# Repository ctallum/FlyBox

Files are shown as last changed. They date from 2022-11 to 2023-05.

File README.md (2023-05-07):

# FlyBox - Olin Brandeis Rosbash Lab HMMI FlyBox Redesign SCOPE Project

# About the Firmware
All the source code and documentation for the FlyBox firmware can be found [here](https://github.com/ctallum/FlyBox-firmware)

# About the Web UI
All the source code and documentation for the webside can be found [here](https://github.com/ctallum/FlyBox/tree/main/programming-gui)

## Test Creator Website
To access the website, visit:
https://rosbash-lab-flybox.github.io/FlyBox/

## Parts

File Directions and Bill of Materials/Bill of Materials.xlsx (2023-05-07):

 |  | FlyBox Bill of Materials |  | Total Items | Total Cost | Chris Allum, Olivia Jo Bradley, S. C. "Mack" McAneney, Zachary Sherman, Florian Schwarzinger
 |  |  |  | 207 | $735.16
Subsystem | Custom | Item | Cost Per Unit | Quantity | Total Cost | Source | Notes
PCB | TRUE | Main PCB | $80.00 | 1 | $61.41 | PCBWay (https://www.pcbway.com/project/shareproject/W547848AS1D13_MainBoardGerber3_5fe985dc.html) | Price with assembly and an order size of 5, may change slightly
PCB | TRUE | IR and fans PCB | $50.00 | 1 | $43.14 | PCBWay (https://www.pcbway.com/project/shareproject/FlyBox_IR_Board_50aa739c.html) | Price with assembly and an order size of 5, may change slightly
PCB | TRUE | RGW LED PCB | $50.00 | 1 | $51.54 | PCBWay (https://www.pcbway.com/project/shareproject/FlyBox_RGW_Board_fc0900b7.html) | Price with assembly and an order size of 5, may change slightly
Miscellaneous | FALSE | Zipties | $6.99 | 1 | $6.99 | Amazon (http://www.amzn.com/B08TVLYB3Q)
Miscellaneous | FALSE | IR filter for camera | $0.05 | 1 | $0.05 | ePlastics (https://www.eplastics.com/plexiglass/acrylic-sheets/ACRY31430-125PM11-555X11-850) | We believe this product will work, but we have been using filters provided by Brandeis
Miscellaneous | FALSE | Electric screwdriver | $25.99 | 1 | $25.99 | Amazon (https://www.amazon.com/Electric-Screwdriver-Cordless-Precision-Rechargeable/dp/B08X9V5K2V)
Miscellaneous | FALSE | Cyanoacrylate glue | $13.99 | 1 | $13.99 | Amazon (https://www.amazon.com/dp/B01MDNS8QB?tag=architecture_lab-20&linkCode=ogi&th=1)
Frame Raw Materials | FALSE | 12"x24"x1/4" black acrylic sheet | $21.13 | 6 | $126.78 | McMaster (https://www.mcmaster.com/8505K755-8505K923/)
Frame Raw Materials | FALSE | 1/8" translucent white acrylic (12"x24" sheet) | $15.40 | 1 | $15.40 | McMaster (https://www.mcmaster.com/8505K742/)
Frame Raw Materials | FALSE | Black felt (≥13"x13") | $4.50 | 1 | $4.50 | Amazon (https://www.amzn.com/B07MPQ29TB) | One sheet of felt has enough material for four boxes
Frame Raw Materials | TRUE | 3D print - fan baffle |  | 2 | $0.00 | n/a
Frame Raw Materials | TRUE | 3D print - camera mount |  | 1 | $0.00 | n/a
Frame Raw Materials | TRUE | 3D print - SD card and rotary encoder piece |  | 1 | $0.00 | n/a
Frame Raw Materials | TRUE | 3D print - display and PCB spacer |  | 14 | $0.00 | n/a
Frame Raw Materials | FALSE | J-B Weld 31319 RTV silicone | $7.45 | 1 | $7.45 | Amazon (https://www.amzn.com/B00ID8F8E4)
Frame Hardware | FALSE | Feet (with provided screws) | $1.00 | 4 | $4.00 | Amazon (https://www.amzn.com/B08PCGXKK9) | Come in 12 pack
Frame Hardware | FALSE | Acrylic hinges | $0.42 | 2 | $0.85 | Amazon (https://www.amzn.com/B09B3GNV9T) | Come in 20 pack
Frame Hardware | FALSE | Latch | $2.25 | 1 | $2.25 | Amazon (http://www.amzn.com/B01MR126O6) | Come in 4 pack
Frame Hardware | FALSE | M2x6 cap head screw | $0.10 | 4 | $0.39 | McMaster (https://www.mcmaster.com/91292A831/)
Frame Hardware | FALSE | M3x12 round head screw | $0.07 | 8 | $0.54 | McMaster (https://www.mcmaster.com/92095A183/) | Come in 100 pack
Frame Hardware | FALSE | M3x16 round head screw | $0.09 | 20 | $1.86 | McMaster (https://www.mcmaster.com/92095A184/) | Come in 100 pack
Frame Hardware | FALSE | M3x20 round head screw | $0.11 | 28 | $2.97 | McMaster (https://www.mcmaster.com/92095A185/) | Come in 50 pack
Frame Hardware | FALSE | M3x35 standoff | $2.91 | 4 | $11.64 | McMaster (https://www.mcmaster.com/95947A519/)
Frame Hardware | FALSE | M3 nut | $0.03 | 48 | $1.26 | McMaster (https://www.mcmaster.com/90592A085/) | Come in 100 pack
Frame Hardware | FALSE | M4x12 round head screw | $0.13 | 2 | $0.27 | McMaster (https://www.mcmaster.com/92095A192/) | Come in 100 pack
Frame Hardware | FALSE | M4x20 round head screw | $0.17 | 2 | $0.35 | McMaster (https://www.mcmaster.com/92095A196/) | Come in 50 pack
Frame Hardware | FALSE | M4 nut | $0.03 | 4 | $0.13 | McMaster (https://www.mcmaster.com/90592A090/) | Come in 100 pack
Electronics | FALSE | USB A-male to micro-B-male cable - 6 feet | $7.41 | 1 | $7.41 | Amazon (https://www.amazon.com/AmazonBasics-Male-Micro-Cable-Black/dp/B07232M876?th=1)
Electronics | FALSE | ESP32 microcontroller | $7.00 | 1 | $7.00 | Amazon (https://www.amzn.com/B09GK74F7N)
Electronics | FALSE | SPI SD card reader | $0.89 | 1 | $0.89 | Amazon (https://www.amzn.com/B0B7WZQVHS) | "Welding" should be selected to avoid needing to solder
Electronics | FALSE | RTC DS3231 real time clock | $4.60 | 1 | $4.60 | Amazon (http://www.amzn.com/B09KPC8JZQ)
Electronics | FALSE | Bi-directional logic level converter | $7.95 | 1 | $7.95 | Adafruit (https://www.adafruit.com/product/395)
Electronics | FALSE | 12V DC buck converter | $7.50 | 1 | $7.50 | Amazon (http://www.amzn.com/B07XXWQ49N)
Electronics | FALSE | 20x4 I2C display module | $10.99 | 1 | $10.99 | Amazon (http://www.amzn.com/B07QLRD3TM)
Electronics | FALSE | 3021-D-E-1000 BuckPuck | $10.99 | 4 | $43.96 | LuxeonStar (https://www.luxeonstar.com/1000ma-externally-dimmable-buckpuck-dc-driver)
Electronics | FALSE | 5K audio potentiometer | $2.50 | 1 | $2.50 | Adafruit (https://www.adafruit.com/product/5284)
Electronics | FALSE | Red LED strip | $11.88 | 1 | $11.88 | Waveform (https://store.waveformlighting.com/collections/led-strips/products/simplecolor-red-led-strip-lights) | Only using a fraction of the roll per box
Electronics | FALSE | Green LED strip | $11.88 | 1 | $11.88 | Waveform (https://store.waveformlighting.com/collections/simplecolor/products/simplecolor-green-led-strip-lights) | Only using a fraction of the roll per box
Electronics | FALSE | White LED strip | $6.81 | 1 | $6.81 | Waveform (https://store.waveformlighting.com/collections/led-strips/products/filmgrade-led-strip-lights-for-film-photography?variant=13809653186662) | Only using a fraction of the roll per box
Electronics | FALSE | IR LED strip | $12.64 | 1 | $12.64 | Waveform (https://store.waveformlighting.com/collections/led-strips/products/infrared-850-nm-ir-led-strip-light?variant=13726854578278) | Only using a fraction of the roll per box
Electronics | FALSE | LED strip clasps | $0.96 | 13 | $12.47 | Amazon (https://www.amazon.com/Solderless-Connector-Terminal-Screwdriver-Included/dp/B09Y91QCQR)
Electronics | FALSE | Assorted breadboard jumper wires | $6.99 | 1 | $6.99 | Amazon (http://www.amzn.com/B07GD2BWPY)
Electronics | FALSE | Noctua NF-A4x10 PWM fans | $14.95 | 4 | $59.80 | Amazon (https://www.amzn.com/B07DXRNYNX)
Electronics | FALSE | Power switch | $0.58 | 1 | $0.58 | Amazon (https://www.amzn.com/B08Q3WJW8Q)
Electronics | FALSE | DC power jack | $1.52 | 1 | $1.52 | Amazon (https://www.amazon.com/5-5mm-Supply-Socket-Female-Connection/dp/B082GHXS1Q) | Pack of 5, only using one per box
Electronics | FALSE | Rotary encoder | $2.00 | 1 | $2.00 | Amazon (https://www.amzn.com/B07F26CT6B)
Electronics | FALSE | Adafruit 4121 USB passthrough | $5.95 | 1 | $5.95 | Adafruit (https://www.adafruit.com/product/4212)
Electronics | FALSE | USB A-male to B-male cable - 6 feet | $6.29 | 1 | $6.29 | Amazon (https://www.amzn.com/B00NH11KIK)
Electronics | FALSE | Logitech C920 webcam | $64.90 | 1 | $64.90 | Amazon (http://www.amzn.com/B006JH8T3S)
Electronics | FALSE | 90 degree pin headers | $8.49 | 1 | $8.49 | Amazon (https://www.amazon.com/Generic-Female-Header-Arduino-LilyPad/dp/B00OE8GTQ8)
Electronics | FALSE | Male barrel jack adapter | $5.97 | 1 | $5.97 | Amazon (https://www.amazon.com/Barrel-Connector-Cameras-Single-LED/dp/B01M1YA9ST?s=electronics)
Electronics | FALSE | WAGO solderless inline wire connector | 25.39 | 1 | 25.39 | Amazon (https://www.amazon.com/221-2401-WAGO-Lever-Nuts%C2%AE-2-Conductor-Transparent/dp/B0BKR2SR7H) | Only using a few per box
Electronics | FALSE | RTC battery | $7.59 | 1 | $7.59 | Amazon (https://www.amazon.com/Procter-Gamble-DURDL2032B4PK-Duracell-Lithium/dp/B009108SGS?s=electronics) | Only using one per box
Electronics | FALSE | Ribbon Wire | $1.00 | 1 | $1.00 | Amazon (https://www.amazon.com/AOTOINK-Conductor-Extension-Welding-Tinned/dp/B08JTZCJV1) | Only using a fraction of the roll per box
Electronics | FALSE | Power supply | $6.50 | 1 | $6.50 | Amazon (https://www.amazon.com/100-240V-Transformers-Switching-Applications-Connectors/dp/B077PW5JC3?s=electronics) | Pack of 2, only using 1

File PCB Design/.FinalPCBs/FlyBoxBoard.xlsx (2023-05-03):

 |  |  | T-1D14W547848A BOM
Item # | *Designator | *Qty | Manufacturer | *Mfg Part # | Description / Value | *Package/Footprint | Type | Your Instructions / Notes
1 | 5V in, 12V in, RED, GREEN, INFRARED, WHITE | 6 | Würth Elektronik, from digikey | 691213510002 | 2 Pin 5.08 screw terminal |  | Thru Hole | Arrange the component so the screw terminals face the outer edge of the board
2 | FANS, LCD Screen | 2 | Würth Elektronik, from digikey | 691241510004 | 4 Pin 5.08 screw terminal |  | Thru Hole | Arrange the component so the screw terminals face the outer edge of the board
3 | Hours, Minutes | 2 | TE Connectivity ALCOSWITCH Switches | 1571563-2 | SWITCH TACTILE SPST-NO 0.05A 24V | SW_1571563-2 | SMD
4 | BuckPuck IR, BuckPuck Green, BuckPuck Red, BuckPuck White | 4 | Sullins Connector Solutions | PPPC071LFBN-RC | CONN HDR 7POS FEMALE |  | Thru Hole
5 | Logic Level Right Side HV, Logic Level Left Side HV, | 2 | Würth Elektronik, from digikey | 61301011821 | CONN HDR 10POS FEMALE |  | Thru Hole
5 | 5V, 12V, ESP 32 unused pins, Potentiometer, Potentiometer, GND, ESP 32 unused pins, | 7 | Würth Elektronik, from digikey | 61300511821 (https://www.pcbway.com/components/detail/61300511821/732960/) | CONN HDR 5POS FEMALE |  | Thru Hole
6 | Real Time Controller | 1 | Würth Elektronik, from digikey | 61300611821 (https://www.pcbway.com/components/detail/61300611821/437679/) | CONN HDR 6POS FEMALE |  | Thru Hole
7 | ESP 32 Left Side extra pinouts | 1 | Würth Elektronik, from digikey | 62000211821 (https://www.digikey.com/en/products/detail/w%C3%BCrth-elektronik/62000211821/15672178) | CONN HDR 2POS FEMALE |  | Thru Hole
8 | Logic Level LV pins, Logic Level HV pins | 2 | Würth Elektronik, from digikey | 61300311821 (https://www.pcbway.com/components/detail/61300311821/1044014/) | CONN HDR 3POS FEMALE |  | Thru Hole
9 | ESP 32 Left Side, ESP 32 Right Side | 2 | Sullins Connector Solutions | PPTC151LFBN-RC | CONN HDR 15POS FEMALE |  | Thru Hole
10 | 5KOhms | 8 | Stackpole Electronics Inc (https://www.digikey.com/en/supplier-centers/stackpole-electronics) | RNCP0805FTD4K99 | 5k ohm SMD resistor 0805/2012 metric | 0805 | SMD
 | Rotary Knob | 1 | Phoenix Contact (https://www.digikey.com/en/supplier-centers/phoenix-contact) | 1729157 | 5 Pin 5.08 screw terminal |  | Thru Hole | Arrange the component so the screw terminals face the outer edge of the board
 | SD card reader | 1 | Phoenix Contact (https://www.digikey.com/en/supplier-centers/phoenix-contact) | 1729160 | 6 Pin 5.08 screw terminal |  | Thru Hole | Arrange the component so the screw terminals face the outer edge of the board
 | Transistor, Transistor, Transistor, Transistor | 4 | STMicroelectronics from digikey | 2N3906 (https://www.pcbway.com/components/detail/2N3906/289442/) | 2N3906 Transistor |  | Thru Hole
 | Transistor, Transistor, Transistor, Transistor | 4 | Digikey (Micro Commercial Co) | 2N3906-AP (https://www.pcbway.com/components/detail/2N3906AP/883195/) | 2N3906 Transistor |  | Thru Hole | https://www.pcbway.com/components/detail/2N3906AP/883195/

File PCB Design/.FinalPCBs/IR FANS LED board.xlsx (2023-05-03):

 |  |  | T-1D18W547848A BOM
Item # | *Designator | *Qty | Manufacturer | *Mfg Part # | Description / Value | *Package/Footprint | Type | Your Instructions / Notes
1 | IR, IR, IR, IR from above | 4 | Würth Elektronik, from digikey | 691213510002 | 2 Pin 5.08 screw terminal |  | Thru Hole | Arrange the component so the screw terminals face the outer edge of the board
2 | Fans, Fans, Fans, Fans, | 4 | Würth Elektronik, from digikey | 61300411121 (https://www.digikey.com/en/products/detail/w%C3%BCrth-elektronik/61300411121/4846827) | 4 Pin 2.54 male header pins |  | Thru Hole | Arrange the longer ends of the pins up on the board
2 | Fans from above | 1 | Würth Elektronik, from digikey | 691241510004 | 4 Pin 5.08 screw terminal |  | Thru Hole | Arrange the component so the screw terminals face the outer edge of the board

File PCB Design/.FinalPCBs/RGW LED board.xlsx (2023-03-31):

 |  |  | T-1D16W547848A BOM
Item # | *Designator | *Qty | Manufacturer | *Mfg Part # | Description / Value | *Package/Footprint | Type | Your Instructions / Notes
1 | - R strip +, - G strip +, - R from above +, - W strip +, - G from above +, - W from above +, | 13 | Würth Elektronik, from digikey | 691213510002 | 2 Pin 5.08 screw terminal |  | Thru Hole | Arrange the component so the screw terminals face the outer edge of the board

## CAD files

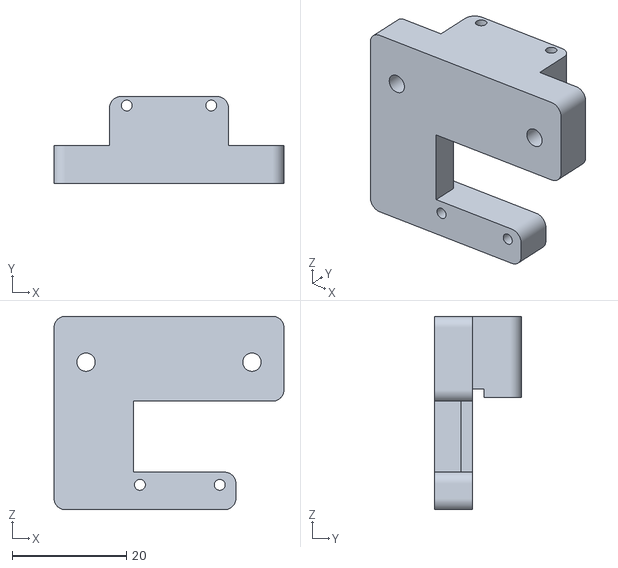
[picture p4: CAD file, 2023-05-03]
fabrication-files/3d-print-files/SD_card_and_rotary_encoder_mount.stl
40.2 x 15.2 x 33.8

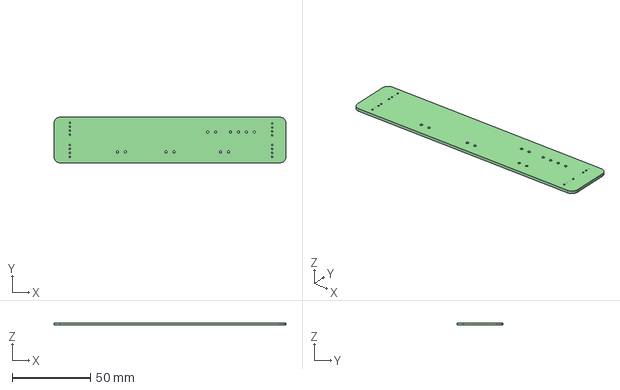
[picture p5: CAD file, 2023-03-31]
PCB Design/IR FANS LED board.step
148.6 x 29.2 x 1.60 mm

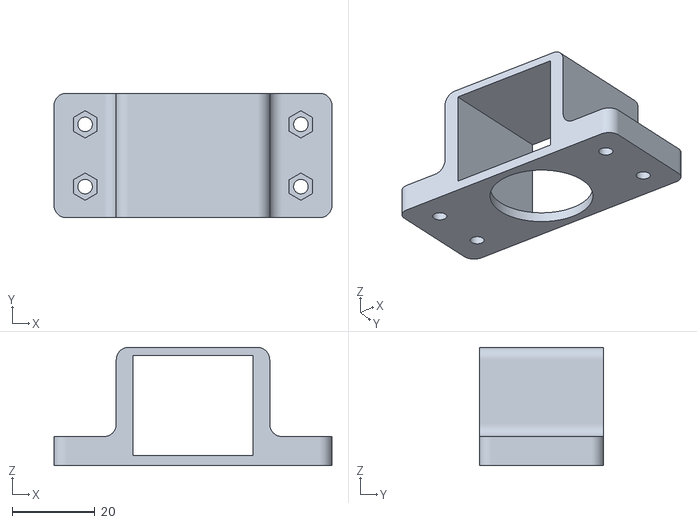
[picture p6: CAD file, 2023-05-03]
fabrication-files/3d-print-files/camera_mount.stl
67.0 x 30.0 x 28.5

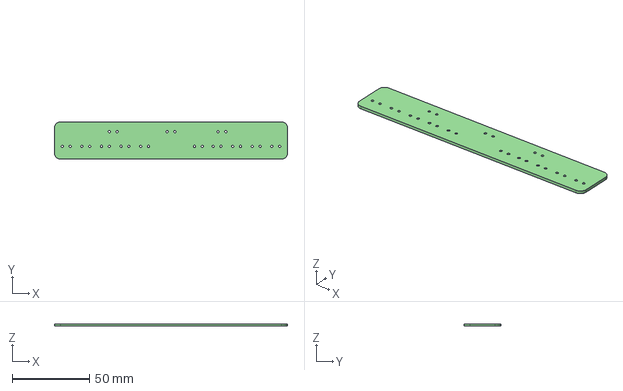
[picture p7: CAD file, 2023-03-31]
PCB Design/RGW LED board.step
151.1 x 24.1 x 1.60 mm

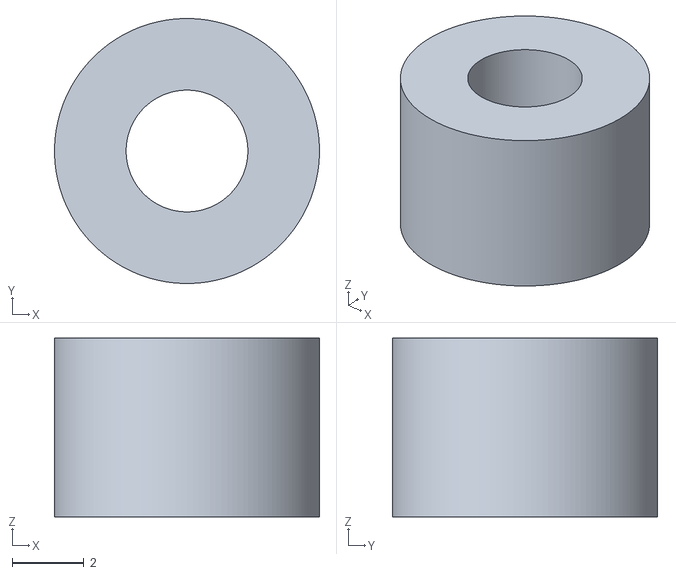
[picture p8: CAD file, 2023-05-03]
fabrication-files/3d-print-files/spacer.stl
7.40 x 7.40 x 4.99

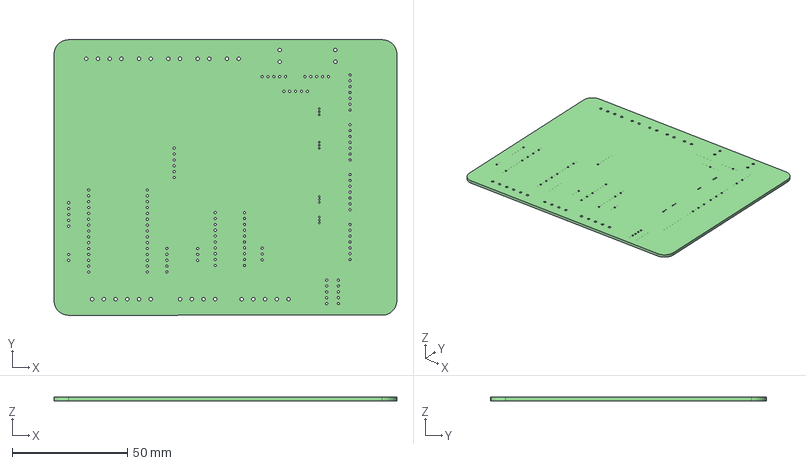
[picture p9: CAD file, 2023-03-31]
PCB Design/FlyBoxBoard.step
148.6 x 119.4 x 1.60 mm

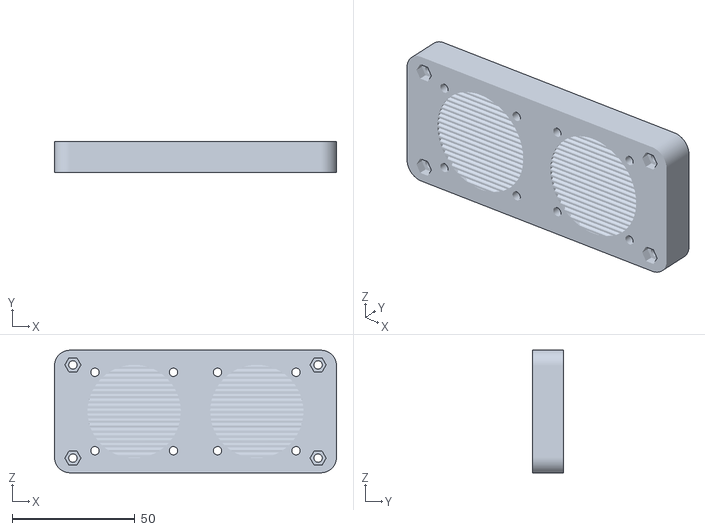
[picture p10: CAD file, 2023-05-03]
fabrication-files/3d-print-files/fan_baffle.stl
115.0 x 12.7 x 50.0

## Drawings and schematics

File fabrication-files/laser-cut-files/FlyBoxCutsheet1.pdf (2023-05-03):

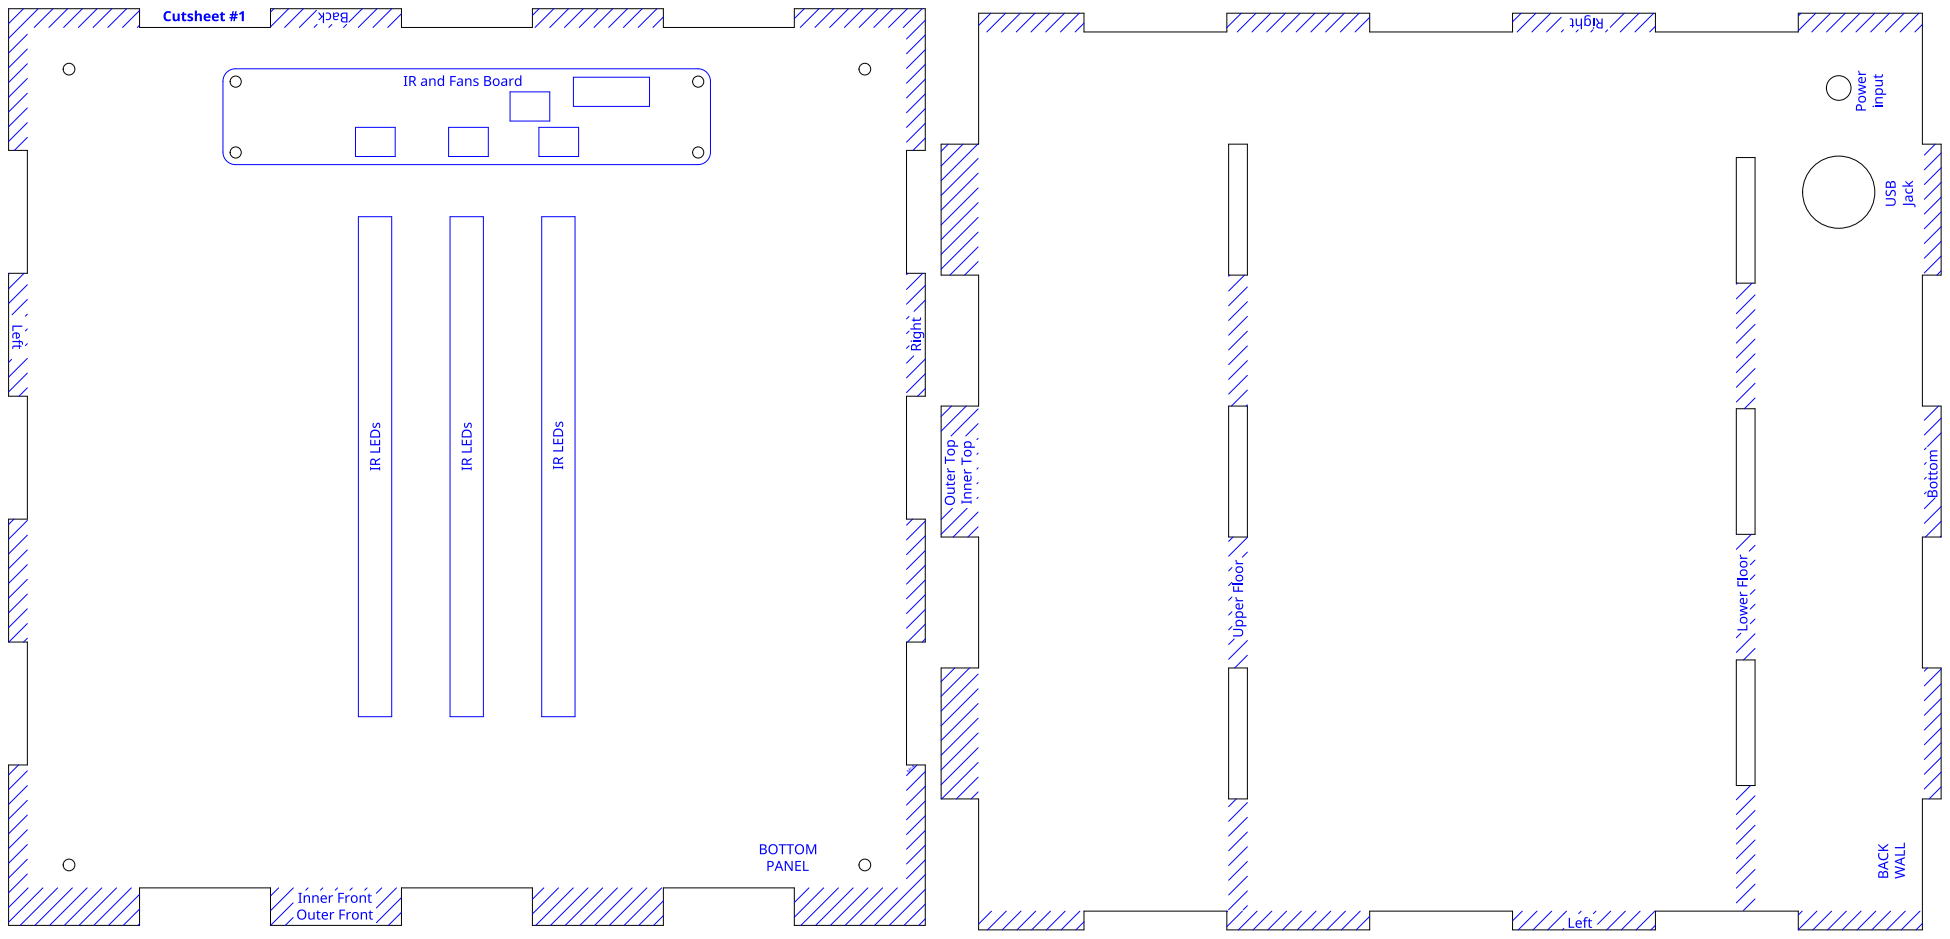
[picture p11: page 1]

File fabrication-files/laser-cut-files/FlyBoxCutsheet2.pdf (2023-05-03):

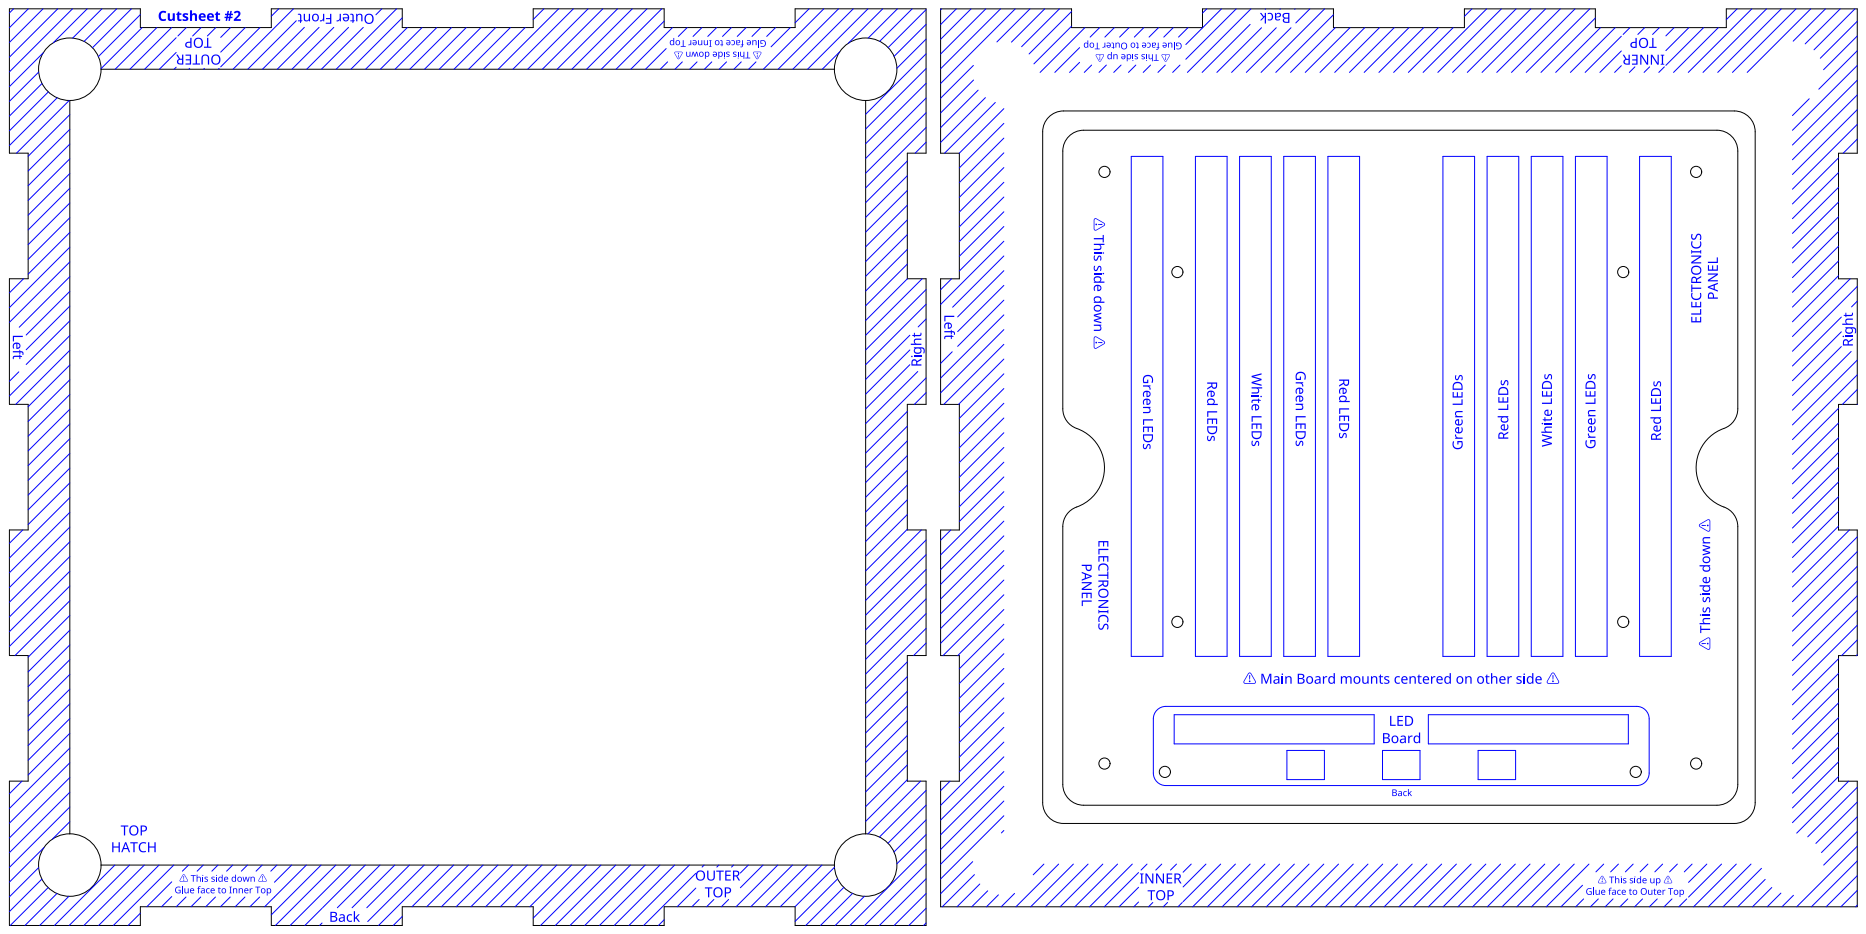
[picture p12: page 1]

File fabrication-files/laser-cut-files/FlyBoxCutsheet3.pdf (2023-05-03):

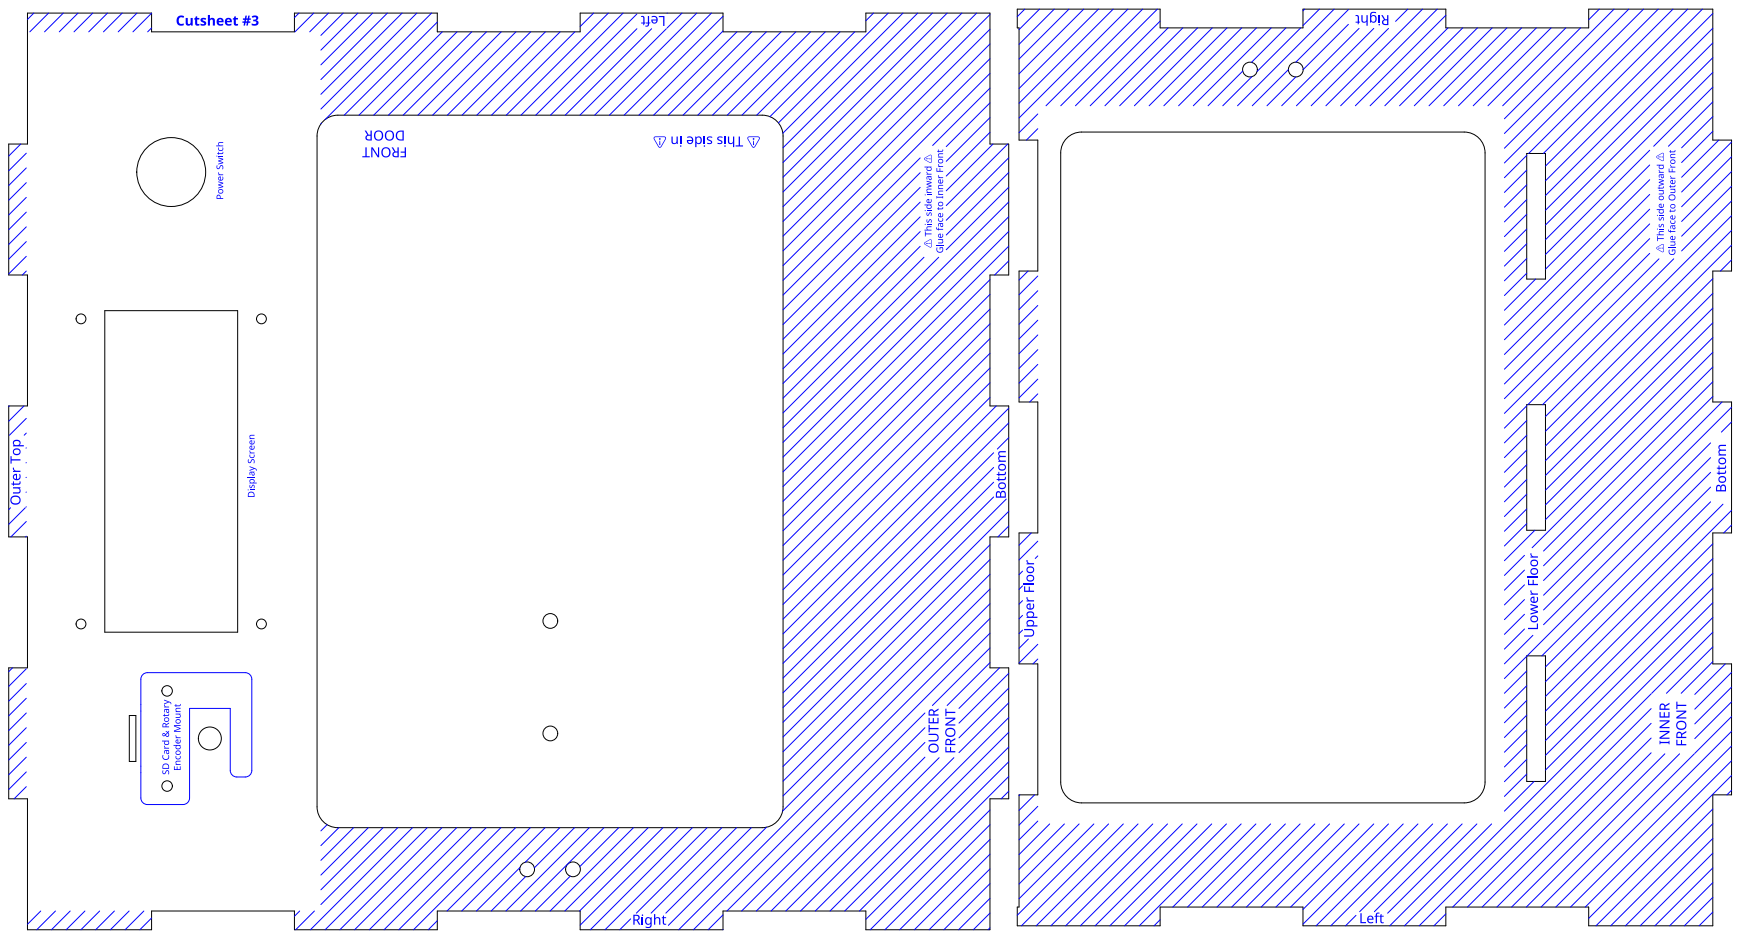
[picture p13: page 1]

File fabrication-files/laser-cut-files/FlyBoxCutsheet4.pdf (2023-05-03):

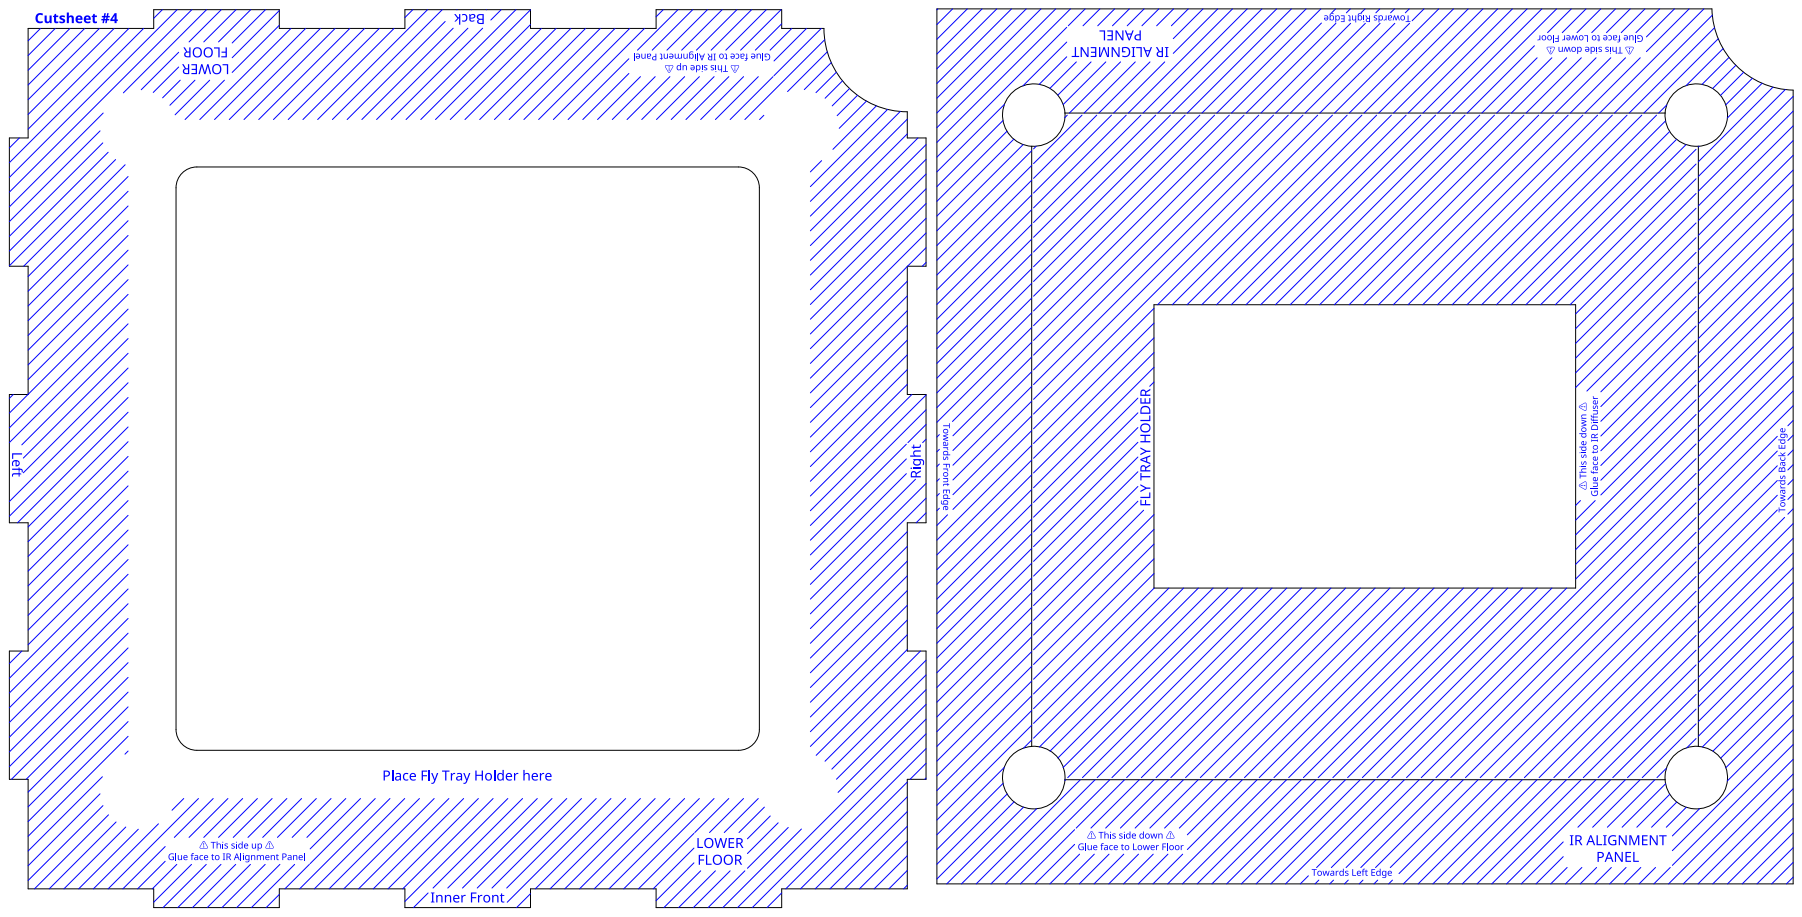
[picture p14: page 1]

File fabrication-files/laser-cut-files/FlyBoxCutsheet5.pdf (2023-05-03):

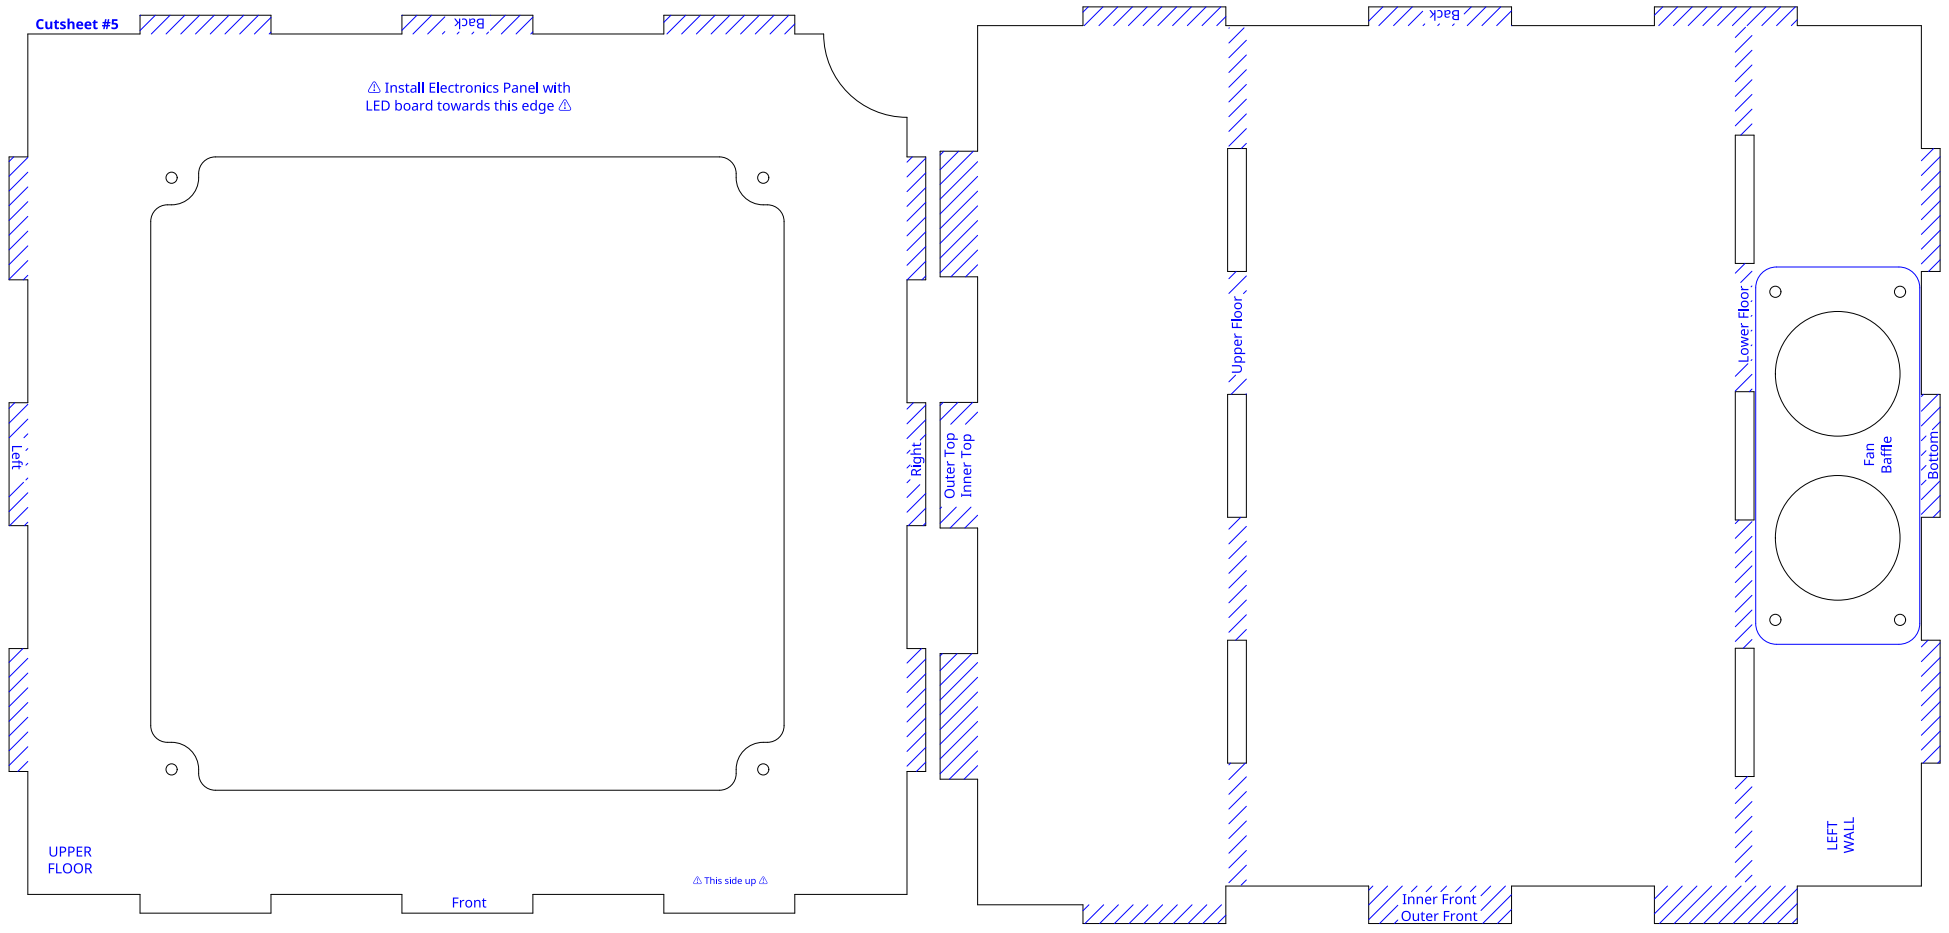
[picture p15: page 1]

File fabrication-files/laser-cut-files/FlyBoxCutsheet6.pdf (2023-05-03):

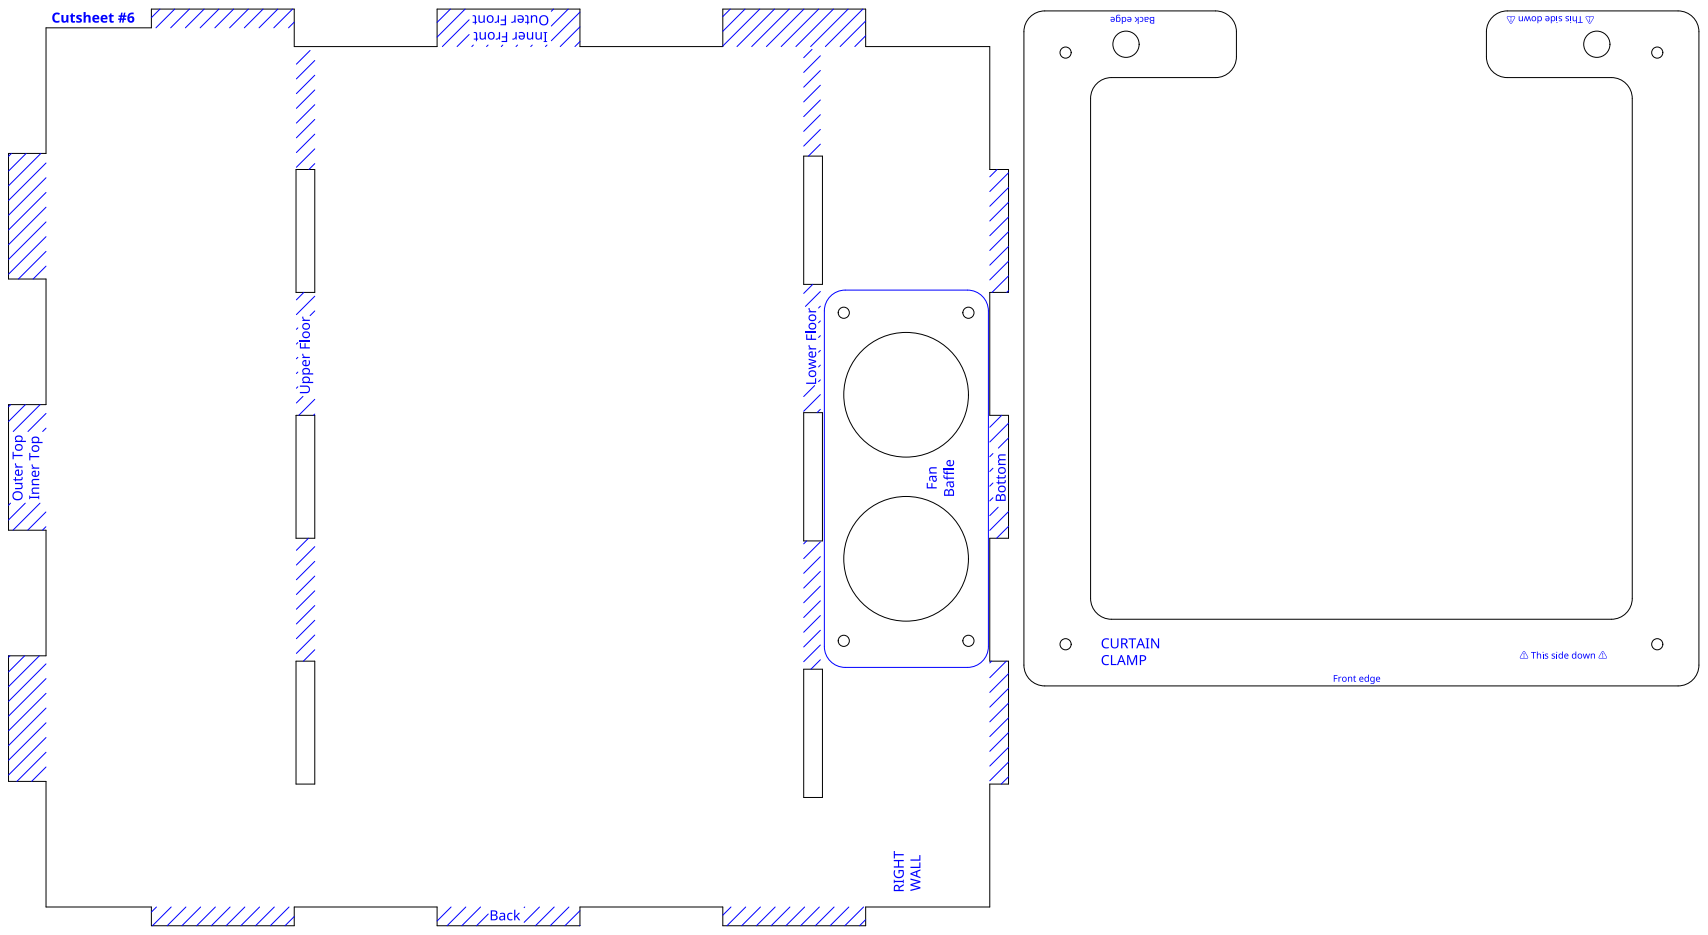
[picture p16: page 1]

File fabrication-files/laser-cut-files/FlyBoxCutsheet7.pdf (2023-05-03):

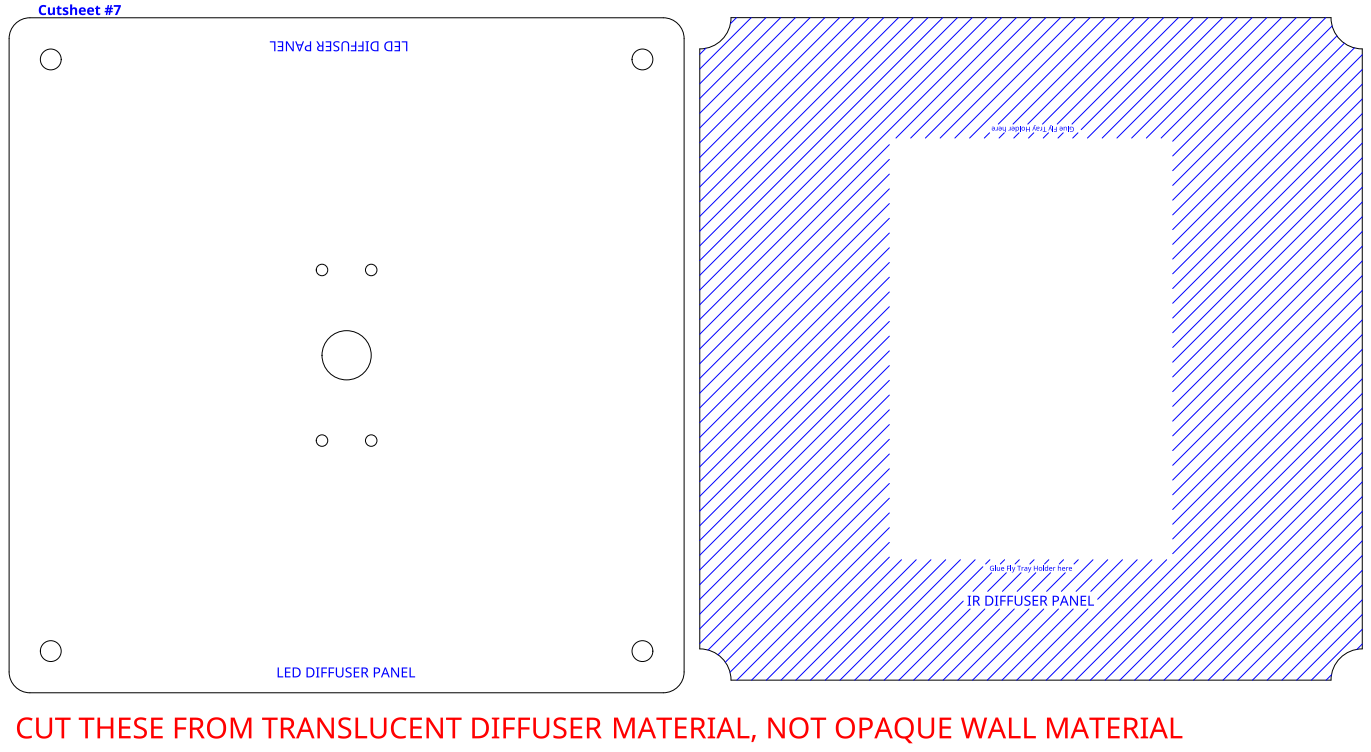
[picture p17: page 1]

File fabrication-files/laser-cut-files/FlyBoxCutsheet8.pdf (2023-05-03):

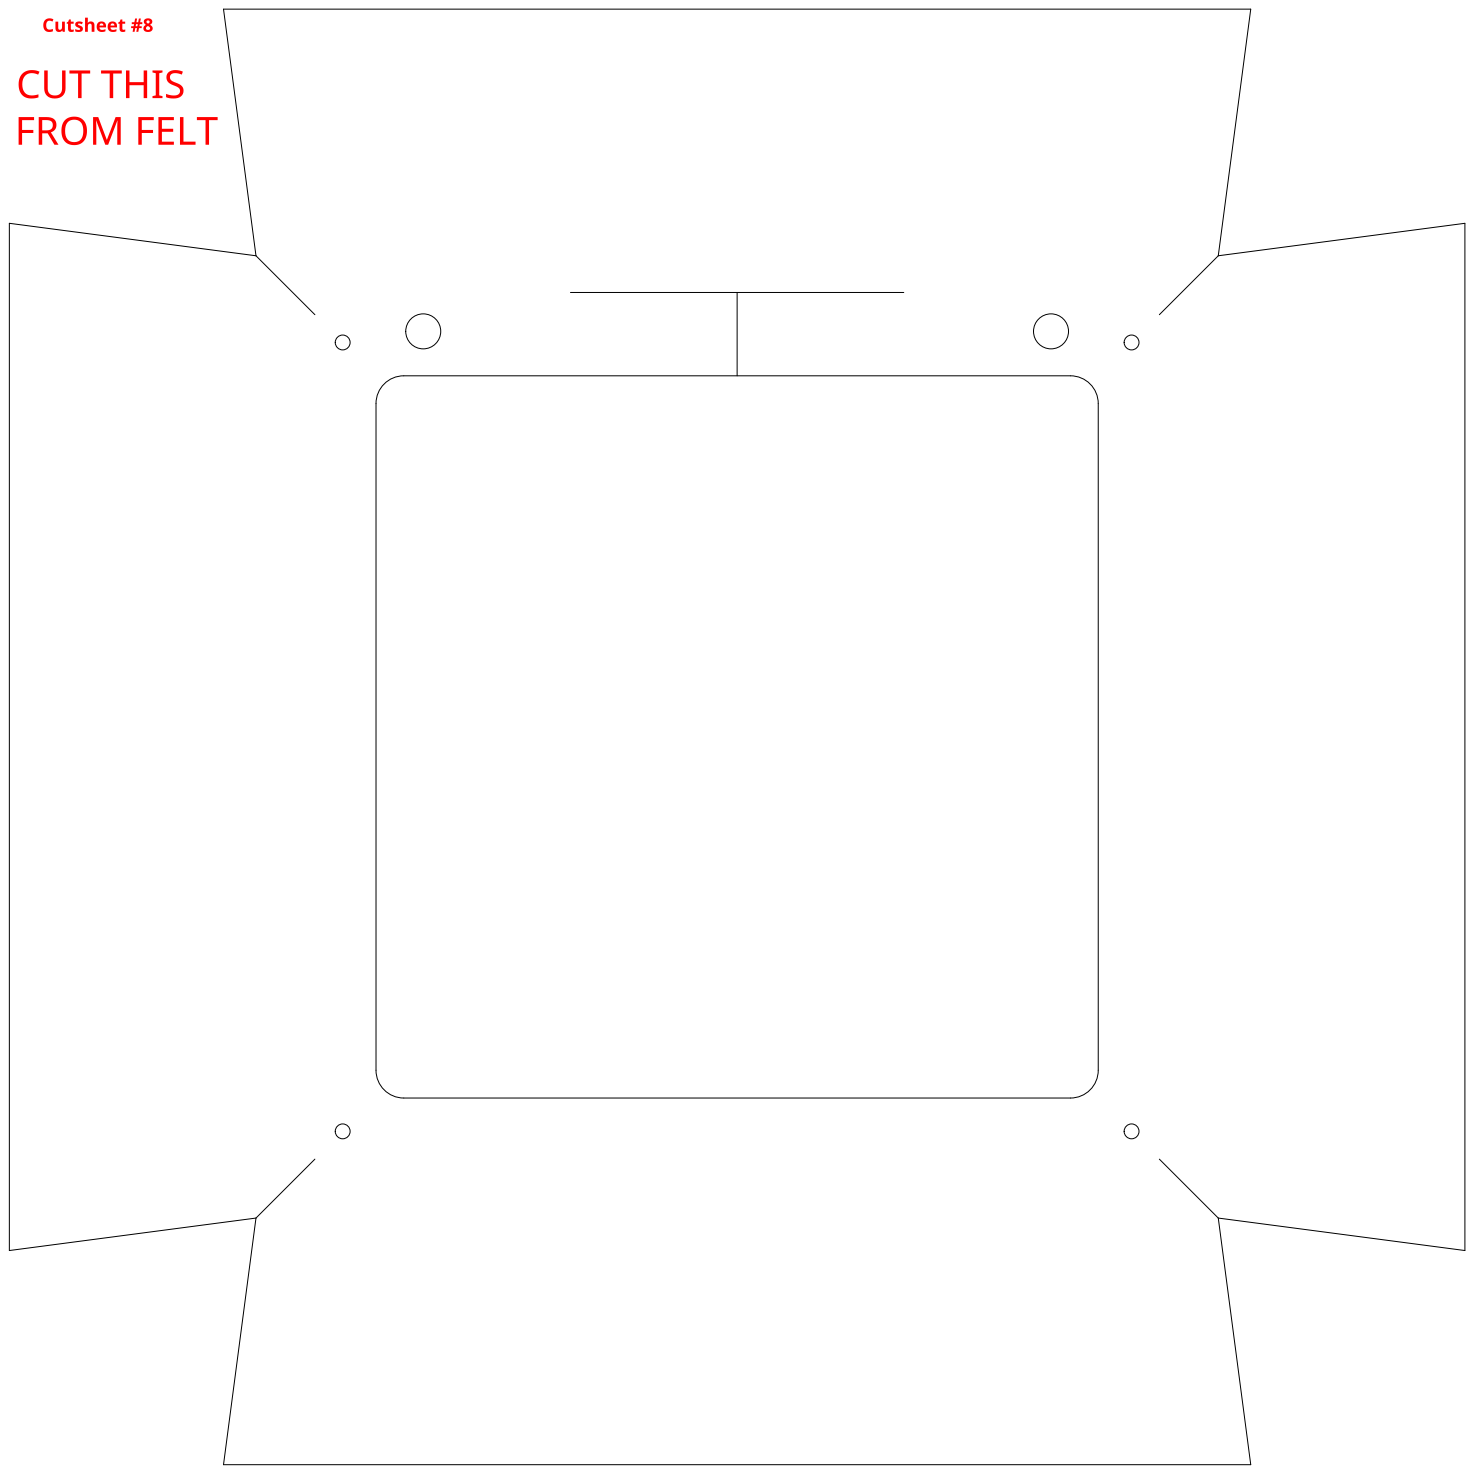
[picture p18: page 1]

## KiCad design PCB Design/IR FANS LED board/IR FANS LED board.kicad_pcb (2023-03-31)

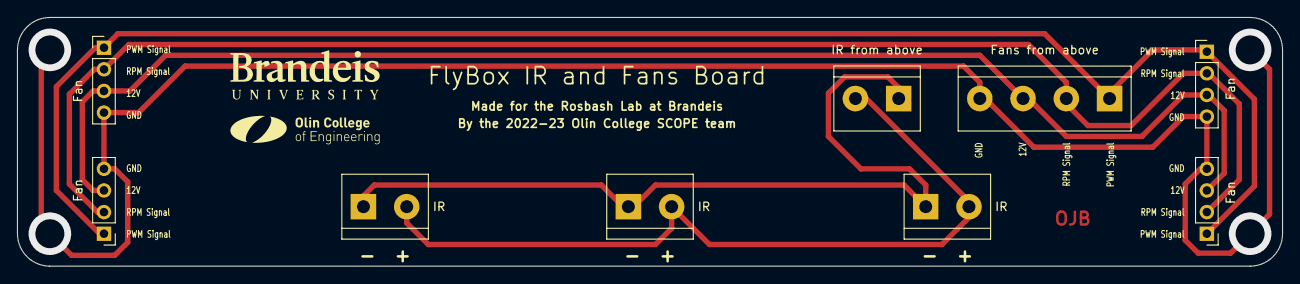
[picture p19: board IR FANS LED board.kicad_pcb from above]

Board: 2 copper layers, 148.6 x 29.2 mm, 9 parts (0 on the bottom side), 6 nets.

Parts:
J1, J2, J8, J9: Fan; PinHeader_1x04_P2.54mm_Vertical
J3, J5, J7: IR; TerminalBlock_bornier-2_P5.08mm
J4: Fans from above; TerminalBlock_bornier-4_P5.08mm
J6: IR from above; TerminalBlock_bornier-2_P5.08mm

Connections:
/12V: J1.3, J2.3, J4.3, J8.3, J9.3
/GND: J1.4, J2.4, J4.4, J8.4, J9.4
/HV5: J1.1, J2.1, J4.1, J8.1, J9.1
/IR LED+: J3.2, J5.2, J6.2, J7.2
/IR LED-: J3.1, J5.1, J6.1, J7.1
/X: J1.2, J2.2, J4.2, J8.2, J9.2

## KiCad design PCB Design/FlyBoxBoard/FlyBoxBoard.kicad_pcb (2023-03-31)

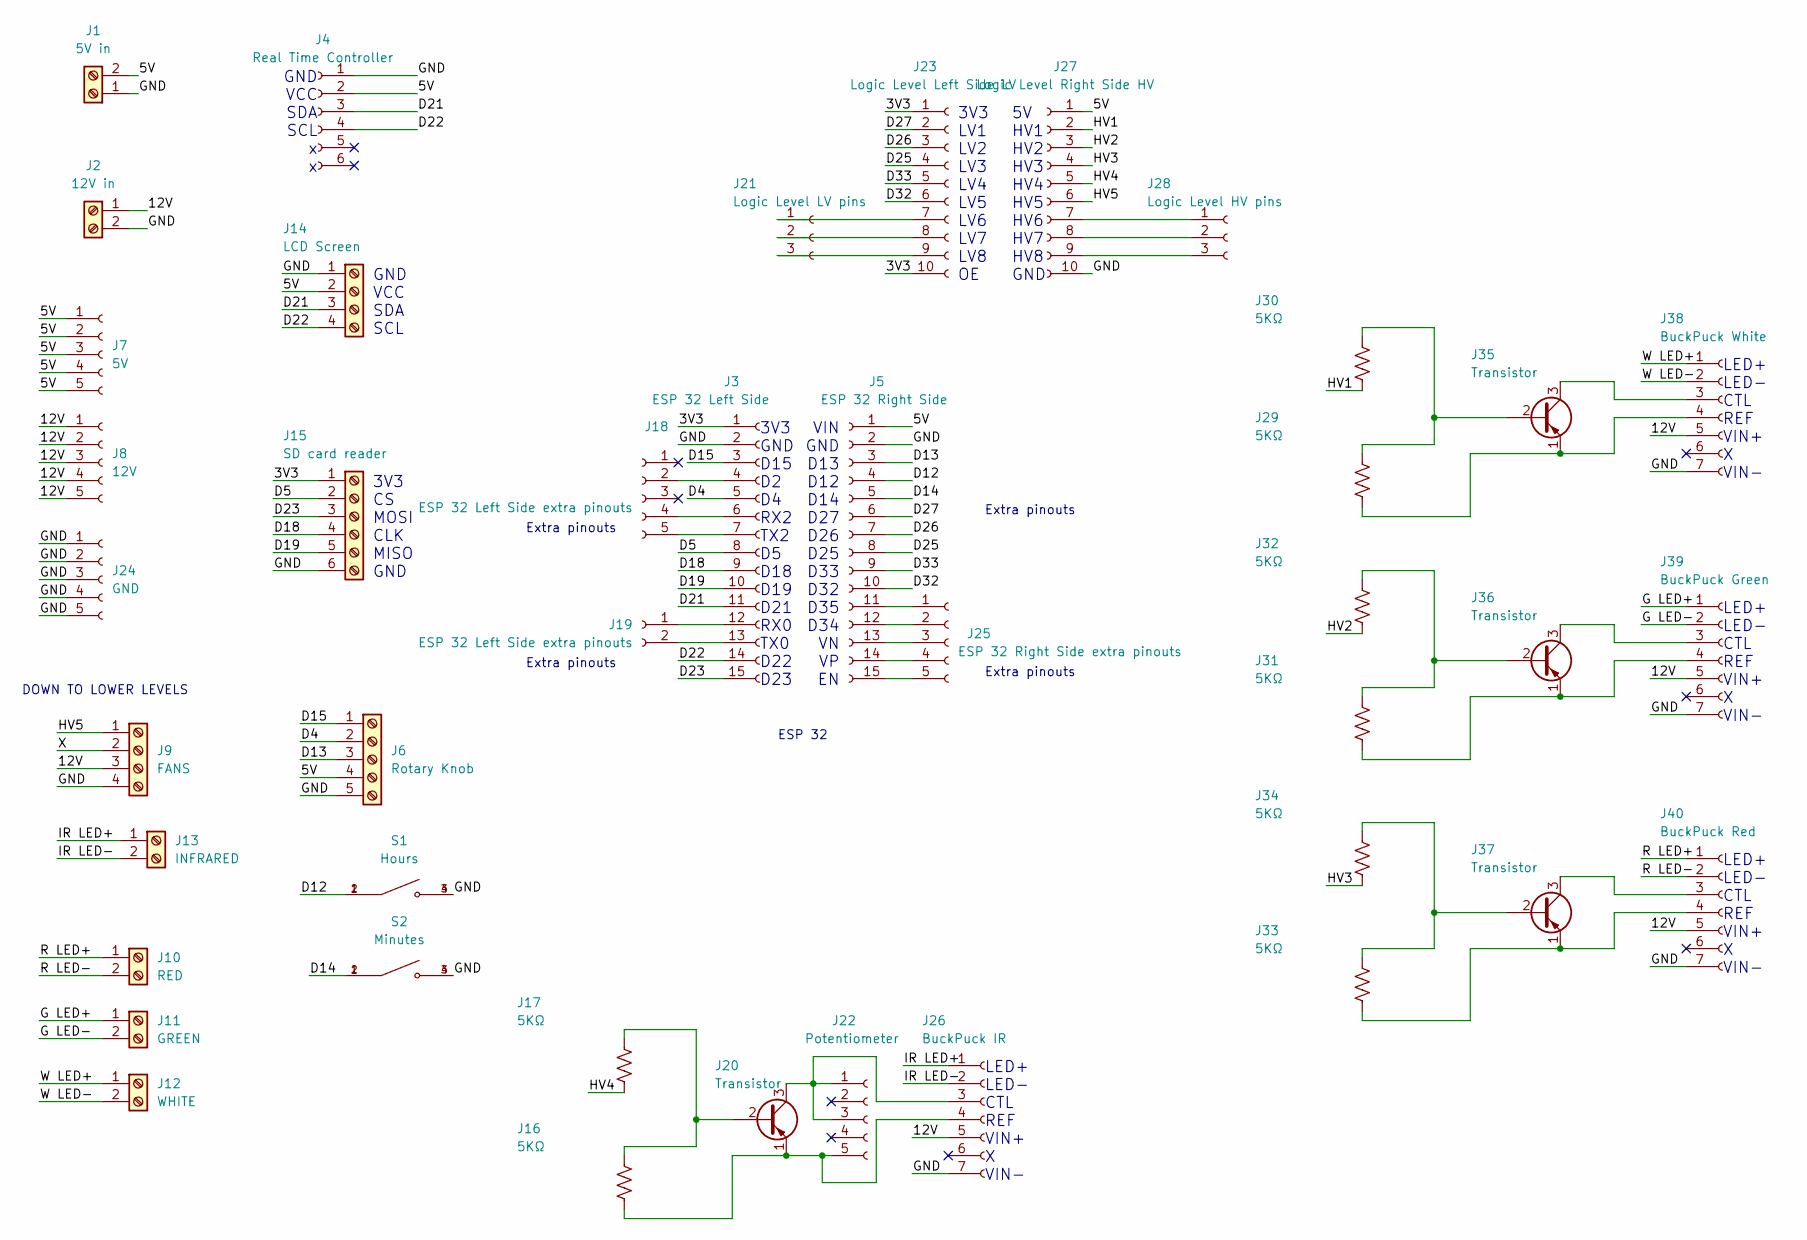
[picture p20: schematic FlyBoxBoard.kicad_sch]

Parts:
J1: 5V in; TerminalBlock_bornier-2_P5.08mm
J2: 12V in; TerminalBlock_bornier-2_P5.08mm
J3: ESP 32 Left Side; PinSocket_1x15_P2.54mm_Vertical
J4: Real Time Controller; PinSocket_1x06_P2.54mm_Vertical
J5: ESP 32 Right Side; PinSocket_1x15_P2.54mm_Vertical
J6: Rotary Knob; TerminalBlock_bornier-5_P5.08mm
J7: 5V; PinSocket_1x05_P2.54mm_Vertical
J8: 12V; PinSocket_1x05_P2.54mm_Vertical
J9: FANS; TerminalBlock_bornier-4_P5.08mm
J10: RED; TerminalBlock_bornier-2_P5.08mm
J11: GREEN; TerminalBlock_bornier-2_P5.08mm
J12: WHITE; TerminalBlock_bornier-2_P5.08mm
J13: INFRARED; TerminalBlock_bornier-2_P5.08mm
J14: LCD Screen; TerminalBlock_bornier-4_P5.08mm
J15: SD card reader; TerminalBlock_bornier-6_P5.08mm
J16, J17, J29, J30, J31, J32, J33, J34: 5KΩ; R_0805_2012Metric_Pad1.20x1.40mm_HandSolder
J18: ESP 32 Left Side extra pinouts; PinSocket_1x05_P2.54mm_Vertical
J19: ESP 32 Left Side extra pinouts; PinSocket_1x02_P2.54mm_Vertical
J20, J35, J36, J37: Transistor; TO-92_Inline
J21: Logic Level LV pins; PinSocket_1x03_P2.54mm_Vertical
J22: Potentiometer; PinSocket_1x05_P2.54mm_Vertical
J23: Logic Level Left Side LV; PinSocket_1x10_P2.54mm_Vertical
J24: GND; PinSocket_1x05_P2.54mm_Vertical
J25: ESP 32 Right Side extra pinouts; PinSocket_1x05_P2.54mm_Vertical
J26: BuckPuck IR; PinSocket_1x07_P2.54mm_Vertical
J27: Logic Level Right Side HV; PinSocket_1x10_P2.54mm_Vertical
J28: Logic Level HV pins; PinSocket_1x03_P2.54mm_Vertical
J38: BuckPuck White; PinSocket_1x07_P2.54mm_Vertical
J39: BuckPuck Green; PinSocket_1x07_P2.54mm_Vertical
J40: BuckPuck Red; PinSocket_1x07_P2.54mm_Vertical
S1: Hours; SW_1571563-2; PARTREV V
S2: Minutes; SW_1571563-2; PARTREV V

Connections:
/3V3: J3.1, J15.1, J23.1, J23.10
/5V: J1.2, J4.2, J5.1, J6.4, J7.1, J7.2, J7.3, J7.4, J7.5, J14.2, J27.1
/12V: J2.1, J8.1, J8.2, J8.3, J8.4, J8.5, J9.3, J26.5, J38.5, J39.5, J40.5
/D4: J3.5, J6.2
/D5: J3.8, J15.2
/D12: J5.4, S1.1, S1.2
/D13: J5.3, J6.3
/D14: J5.5, S2.1, S2.2
/D15: J3.3, J6.1
/D18: J3.9, J15.4
/D19: J3.10, J15.5
/D21: J3.11, J4.3, J14.3
/D22: J3.14, J4.4, J14.4
/D23: J3.15, J15.3
/D25: J5.8, J23.4
/D26: J5.7, J23.3
/D27: J5.6, J23.2
/D32: J5.10, J23.6
/D33: J5.9, J23.5
/G LED+: J11.1, J39.1
/G LED-: J11.2, J39.2
/GND: J1.1, J2.2, J3.2, J4.1, J5.2, J6.5, J9.4, J14.1, J15.6, J24.1, J24.2, J24.3, J24.4, J24.5, J26.7, J27.10, J38.7, J39.7, J40.7, S1.3, S1.4, S2.3, S2.4
/HV1: J27.2, J30.2
/HV2: J27.3, J32.2
/HV3: J27.4, J34.2
/HV4: J17.2, J27.5
/HV5: J9.1, J27.6
/IR LED+: J13.1, J26.1
/IR LED-: J13.2, J26.2
/R LED+: J10.1, J40.1
/R LED-: J10.2, J40.2
/W LED+: J12.1, J38.1
/W LED-: J12.2, J38.2
/X: J9.2
unnamed: J16.1, J17.1, J20.2 (B)
unnamed 35: J16.2, J20.1 (E), J22.5, J26.4; also elsewhere on the board
unnamed: J3.4, J18.2
unnamed: J3.6, J18.4
unnamed: J3.7, J18.5
unnamed: J3.12, J19.1
unnamed: J3.13, J19.2
unnamed 41: J20.3 (C), J22.1, J22.3, J26.3; also elsewhere on the board
unnamed: J21.1, J23.7
unnamed: J21.2, J23.8
unnamed: J21.3, J23.9
unnamed: J5.11, J25.1
unnamed: J5.12, J25.2
unnamed: J5.13, J25.3
unnamed: J5.14, J25.4
unnamed: J5.15, J25.5
unnamed: J27.7, J28.1
unnamed: J27.8, J28.2
unnamed: J27.9, J28.3
unnamed: J29.1, J30.1, J35.2 (B)
unnamed: J29.2, J35.1 (E), J38.4
unnamed: J31.1, J32.1, J36.2 (B)
unnamed: J31.2, J36.1 (E), J39.4
unnamed: J33.1, J34.1, J37.2 (B)
unnamed: J33.2, J37.1 (E), J40.4
unnamed: J35.3 (C), J38.3
unnamed: J36.3 (C), J39.3
unnamed: J37.3 (C), J40.3

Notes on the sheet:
3V3 CS MOSI CLK MISO GND
DOWN TO LOWER LEVELS
VIN GND D13 D12 D14 D27 D26 D25 D33 D32 D35 D34 VN VP EN
GND VCC SDA SCL
3V3 LV1 LV2 LV3 LV4 LV5 LV6 LV7 LV8 OE
5V HV1 HV2 HV3 HV4 HV5 HV6 HV7 HV8 GND
ESP 32
3V3 GND D15 D2 D4 RX2 TX2 D5 D18 D19 D21 RX0 TX0 D22 D23
Extra pinouts
LED+ LED- CTL REF VIN+ X VIN-
GND VCC SDA SCL x x

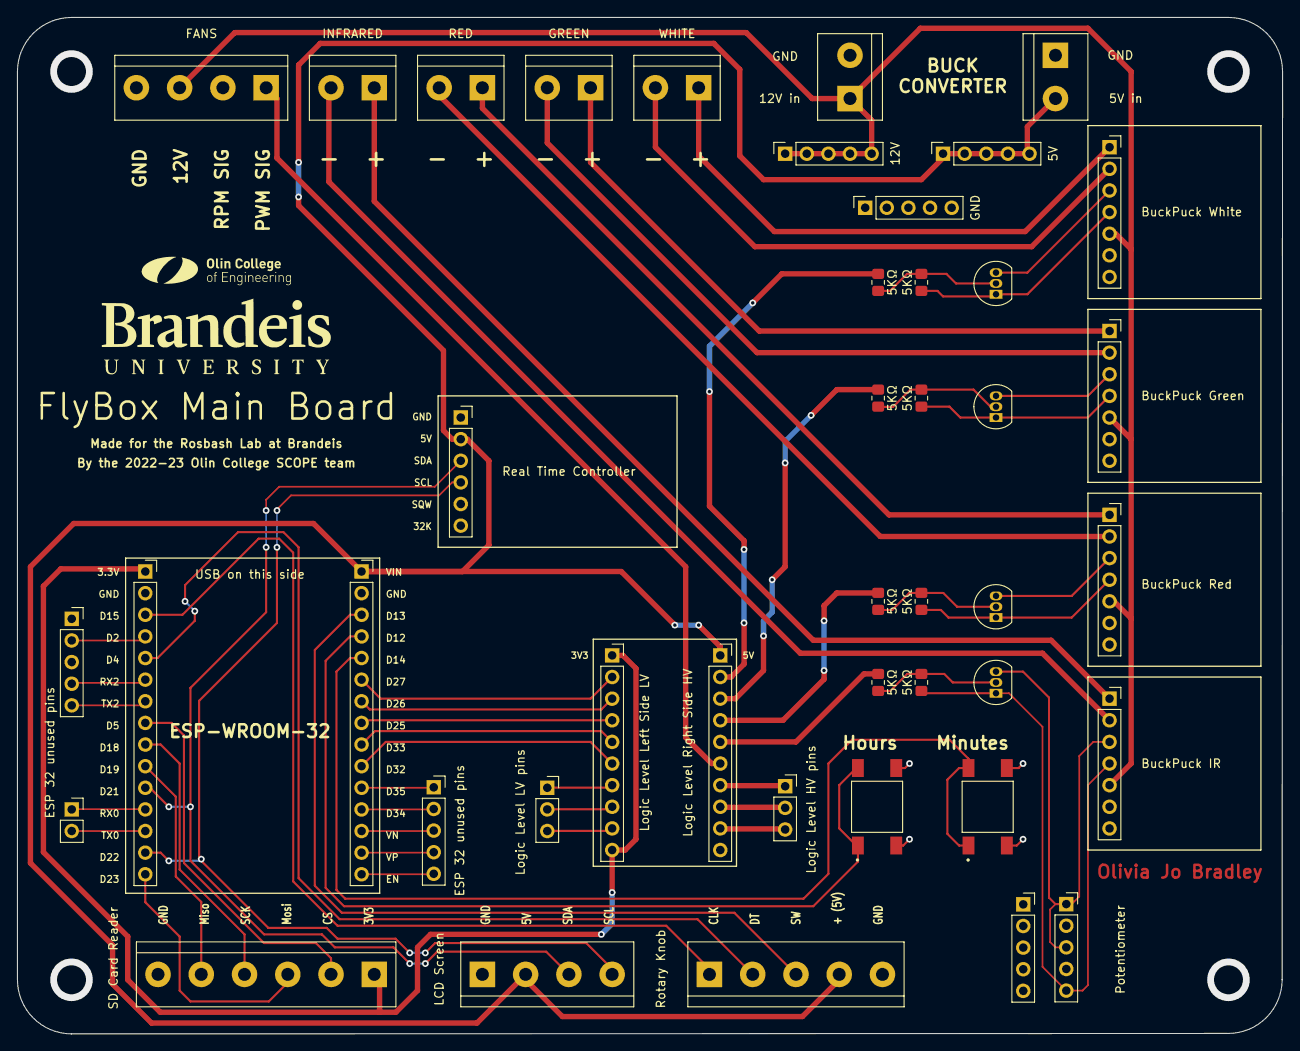
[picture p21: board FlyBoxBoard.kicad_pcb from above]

Board: 2 copper layers, 148.6 x 119.4 mm, 43 parts (0 on the bottom side), 61 nets.

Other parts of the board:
J22#2: Potentiometer; PinSocket_1x05_P2.54mm_Vertical

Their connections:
unnamed 35: J22#2.5; also elsewhere on the board
unnamed 41: J22#2.1, J22#2.3; also elsewhere on the board

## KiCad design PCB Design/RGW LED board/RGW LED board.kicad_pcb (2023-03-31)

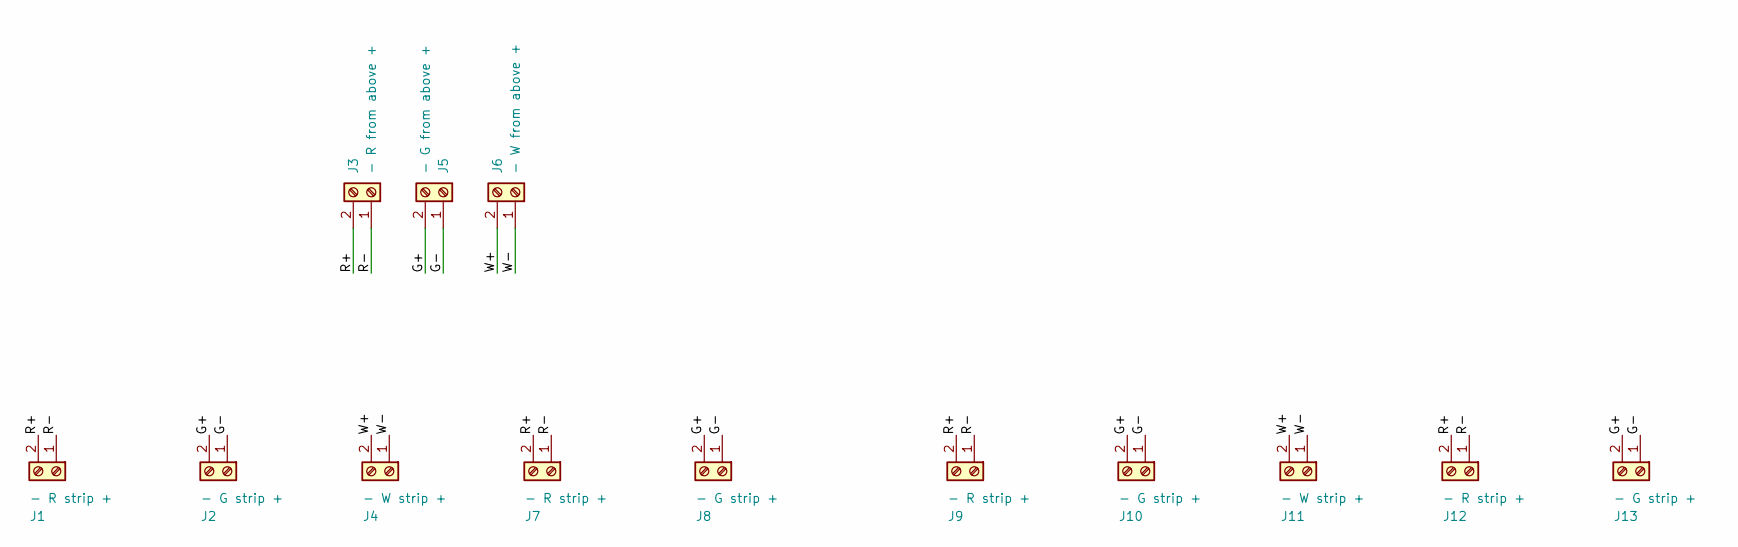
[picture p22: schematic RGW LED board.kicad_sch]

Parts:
J1, J7, J9, J12: - R strip +; TerminalBlock_bornier-2_P5.08mm
J2, J8, J10, J13: - G strip +; TerminalBlock_bornier-2_P5.08mm
J3: - R from above +; TerminalBlock_bornier-2_P5.08mm
J4, J11: - W strip +; TerminalBlock_bornier-2_P5.08mm
J5: - G from above +; TerminalBlock_bornier-2_P5.08mm
J6: - W from above +; TerminalBlock_bornier-2_P5.08mm

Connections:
/G+: J2.2, J5.2, J8.2, J10.2, J13.2
/G-: J2.1, J5.1, J8.1, J10.1, J13.1
/R+: J1.2, J3.2, J7.2, J9.2, J12.2
/R-: J1.1, J3.1, J7.1, J9.1, J12.1
/W+: J4.2, J6.2, J11.2
/W-: J4.1, J6.1, J11.1

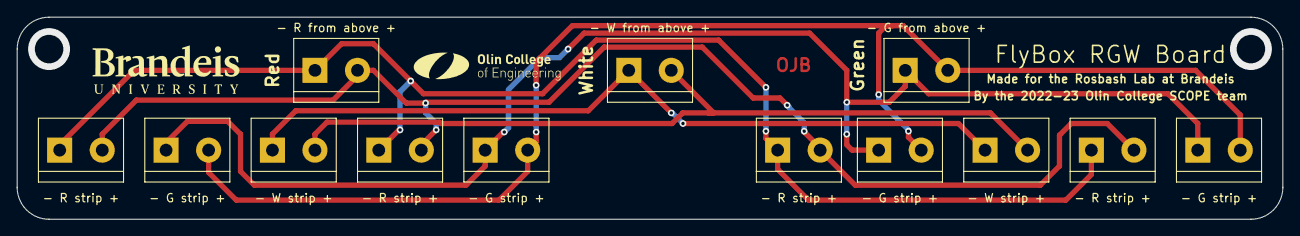
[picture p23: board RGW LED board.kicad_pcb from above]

Board: 2 copper layers, 151.1 x 24.1 mm, 13 parts (0 on the bottom side), 6 nets.

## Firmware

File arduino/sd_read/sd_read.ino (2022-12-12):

#include "header.h"

// set up some global variables for hardware
RTC_DS3231 rtc;
EventList* FlyBoxEvents;

// set up some global variables for timing stuff
int prev_second;
unsigned long sec_elapsed = 0;
unsigned long prev_time = 0;

// set up some global variables for LED Pins
#define WHITE_PIN 26
#define RED_PIN 25
#define GREEN_PIN 27
#define IR_PIN 33

typedef struct PinLayout{
  int Pin;
  bool is_on;
};

// make a dict sort of object so I can use json number to get pin
PinLayout Pins[3] = {PinLayout{RED_PIN, false}, 
                     PinLayout{GREEN_PIN, false}, 
                     PinLayout{WHITE_PIN, false}};

void setup() {

  Serial.begin(115200);
  
  // set up rtc chip
  if (! rtc.begin()) {
  Serial.println("Couldn't find RTC");
  return;
  }
  rtc.adjust(DateTime(__DATE__, __TIME__));
 
  // set up buttons
  init_buttons();

  // set up LCD Screen
  LiquidCrystal_I2C lcd = init_lcd();

  // set up sd card reader
  fs::FS SD = init_SD(lcd);

  // get file name to decode (intro screen)
  char* filename = getFiles(lcd, SD);

  // decode the file via json deserialization
  FlyBoxEvents = DecodeFile(filename);

  
  pinMode(RED_PIN, OUTPUT);
  pinMode(GREEN_PIN, OUTPUT);
  pinMode(WHITE_PIN, OUTPUT);
  pinMode(IR_PIN, OUTPUT);

  digitalWrite(GREEN_PIN, LOW);
  digitalWrite(RED_PIN, LOW);
  digitalWrite(WHITE_PIN, LOW);

  digitalWrite(IR_PIN, HIGH);

  prev_second = 0;
}


void loop() {
  // get current time from RTC chip
  DateTime now = rtc.now();
  int cur_second = now.second();

  // add to elapsed time
  if (cur_second != prev_second){
    sec_elapsed ++;
    prev_second = cur_second;
  }

  // iterate through all the flybox events 
  EventNode* current_event = FlyBoxEvents->root;
  for (int i = 0; i < FlyBoxEvents->n_events; i++) {
    // check if we are during the event
    if (current_event->current->start <= sec_elapsed && current_event->current->stop > sec_elapsed){
      int device = current_event->current->device;
      int frequency = current_event->current->frequency;
      run_event(device, frequency);
    }

    // check the end time
    if (current_event->current->stop == sec_elapsed){
      int device = current_event->current->device;
      kill_event(device);
    }

    current_event = current_event->next;
  }  
}

// int is the GPIO pin the lights are connected to, and freqnecy is in HZ
void run_event(int device, int frequency){
  if (device == 1){
    Serial.println("green flashing");
  }
  int pin = Pins[device].Pin;
  bool is_on = Pins[device].is_on;
  if (frequency == 0){
    digitalWrite(pin, HIGH);
    // Serial.print("Turning on Pin ");
    // Serial.println(pin);
    Pins[device].is_on = true;
    return;
  } 
  else{
    unsigned long current_time = millis();
    int duration = 500/frequency;
    if (current_time - prev_time >= duration){
      prev_time = current_time;
      if (is_on){
        digitalWrite(pin, LOW);
        Pins[device].is_on = false;
      } else{
        Pins[device].is_on = true;
        digitalWrite(pin, HIGH);
      }
    }
  }
}

void kill_event(int device){
  int pin = Pins[device].Pin;
  digitalWrite(pin, LOW);
  Pins[device].is_on = false;
}

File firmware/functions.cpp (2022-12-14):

#include "header.h"

void listDir(fs::FS& fs, const char* dirname, uint8_t levels) {
  Serial.printf("Listing directory: %s\n", dirname);

  File root = fs.open(dirname);
  if (!root) {
    Serial.println("Failed to open directory");
    return;
  }
  if (!root.isDirectory()) {
    Serial.println("Not a directory");
    return;
  }

  File file = root.openNextFile();
  while (file) {
    if (file.isDirectory()) {
      Serial.print("  DIR : ");
      Serial.println(file.name());
      if (levels) {
        listDir(fs, file.name(), levels - 1);
      }
    } else {
      Serial.print("  FILE: ");
      Serial.print(file.name());
      Serial.print("  SIZE: ");
      Serial.println(file.size());
    }
    file = root.openNextFile();
  }
}

void createDir(fs::FS& fs, const char* path) {
  Serial.printf("Creating Dir: %s\n", path);
  if (fs.mkdir(path)) {
    Serial.println("Dir created");
  } else {
    Serial.println("mkdir failed");
  }
}

void removeDir(fs::FS& fs, const char* path) {
  Serial.printf("Removing Dir: %s\n", path);
  if (fs.rmdir(path)) {
    Serial.println("Dir removed");
  } else {
    Serial.println("rmdir failed");
  }
}

void readFile(fs::FS& fs, const char* path) {
  Serial.printf("Reading file: %s\n", path);

  File file = fs.open(path);
  if (!file) {
    Serial.println("Failed to open file for reading");
    return;
  }

  Serial.print("Read from file: ");
  while (file.available()) {
    Serial.write(file.read());
  }
  file.close();
}

void writeFile(fs::FS& fs, const char* path, const char* message) {
  Serial.printf("Writing file: %s\n", path);

  File file = fs.open(path, FILE_WRITE);
  if (!file) {
    Serial.println("Failed to open file for writing");
    return;
  }
  if (file.print(message)) {
    Serial.println("File written");
  } else {
    Serial.println("Write failed");
  }
  file.close();
}

void appendFile(fs::FS& fs, const char* path, const char* message) {
  Serial.printf("Appending to file: %s\n", path);

  File file = fs.open(path, FILE_APPEND);
  if (!file) {
    Serial.println("Failed to open file for appending");
    return;
  }
  if (file.print(message)) {
    Serial.println("Message appended");
  } else {
    Serial.println("Append failed");
  }
  file.close();
}

void renameFile(fs::FS& fs, const char* path1, const char* path2) {
  Serial.printf("Renaming file %s to %s\n", path1, path2);
  if (fs.rename(path1, path2)) {
    Serial.println("File renamed");
  } else {
    Serial.println("Rename failed");
  }
}

void deleteFile(fs::FS& fs, const char* path) {
  Serial.printf("Deleting file: %s\n", path);
  if (fs.remove(path)) {
    Serial.println("File deleted");
  } else {
    Serial.println("Delete failed");
  }
}

void testFileIO(fs::FS& fs, const char* path) {
  File file = fs.open(path);
  static uint8_t buf[512];
  size_t len = 0;
  uint32_t start = millis();
  uint32_t end = start;
  if (file) {
    len = file.size();
    size_t flen = len;
    start = millis();
    while (len) {
      size_t toRead = len;
      if (toRead > 512) {
        toRead = 512;
      }
      file.read(buf, toRead);
      len -= toRead;
    }
    end = millis() - start;
    Serial.printf("%u bytes read for %u ms\n", flen, end);
    file.close();
  } else {
    Serial.println("Failed to open file for reading");
  }


  file = fs.open(path, FILE_WRITE);
  if (!file) {
    Serial.println("Failed to open file for writing");
    return;
  }

  size_t i;
  start = millis();
  for (i = 0; i < 2048; i++) {
    file.write(buf, 512);
  }
  end = millis() - start;
  Serial.printf("%u bytes written for %u ms\n", 2048 * 512, end);
  file.close();
}

Event* NewEvent(int device, int frequency, unsigned long start, unsigned long stop) {
  struct Event* event = (struct Event*)malloc(sizeof(struct Event));

  event->device = device;
  event->frequency = frequency;
  event->start = start;
  event->stop = stop;

  return event;
}

EventNode* NewEventNode(Event* event) {
  struct EventNode* node = (struct EventNode*)malloc(sizeof(struct EventNode));

  node->current = event;
  node->next = NULL;

  return node;
}

EventList* NewEventList() {
  struct EventList* list = (struct EventList*)malloc(sizeof(struct EventList));

  list->root = NULL;
  list->n_events = NULL;

  return list;
}


void AddEvent(EventList* s, EventNode* n) {
  if (s->root == NULL) {
    s->root = n;
  } else {
    EventNode* current_node = s->root;
    while (current_node->next != NULL) {
      current_node = current_node->next;
    }
    current_node->next = n;
  }
  s->n_events++;
}

EventList* DecodeFile(const char* filename) {
  EventList* FlyBoxEvents = NewEventList();
  StaticJsonDocument<256> doc;

  File myFile = SD.open(filename);
  if (myFile) {

    myFile.find("[");
    do {
      DeserializationError error = deserializeJson(doc, myFile);
      if (error) {
        Serial.print(F("deserializeJson() failed: "));
        Serial.println(error.f_str());
      }

      int device = atoi(doc["group"]);
      // int string_len = strlen(device);

      // char* const_device = (char*)malloc(string_len * sizeof(char));
      // strcpy(const_device, device);

      int frequency = doc["itemProps"]["frequency"];
      unsigned long start = doc["start"];
      unsigned long stop = doc["end"];

      // Time* time_start = ConvertTime(start);
      // Time* time_stop = ConvertTime(stop);

      Event* event = NewEvent(device, frequency, start/1000, stop/1000);
      EventNode* event_node = NewEventNode(event);

      AddEvent(FlyBoxEvents, event_node);

    } while (myFile.findUntil(",", "]"));
  }
  return FlyBoxEvents;
}

LiquidCrystal_I2C init_lcd(LiquidCrystal_I2C lcd) {
  

  lcd.init();
  lcd.clear();
  lcd.backlight();  // Make sure backlight is on
  return lcd;
}

void writeLCD(LiquidCrystal_I2C lcd, char* s, int x, int y) {
  lcd.setCursor(x, y);
  lcd.print(s);
}

char* getFiles(LiquidCrystal_I2C lcd, fs::FS& fs) {

  int indicator = 0;
  int prev_up = 0;
  int prev_down = 0;
  int select = 0;
  int disp = 0;

  // get list of files
  char* files[100];

  File root = fs.open("/");
  if (!root) {
    Serial.println("Failed to open directory");
    return "";
  }
  if (!root.isDirectory()) {
    Serial.println("Not a directory");
    return "";
  }

  File file = root.openNextFile();
  int level = 0;
  while (file) {
    if (file.isDirectory()) {
    } else {
      files[level] = (char*)malloc(100 * sizeof(char));
      strcpy(files[level], file.name());
      level++;
    }
    file = root.openNextFile();
  }

  int n_files = level - 1;

  for (;;) {
    int up = !digitalRead(BUTTON_UP);
    int down = !digitalRead(BUTTON_DOWN);
    int enter = !digitalRead(BUTTON_ENTER);
    
    if (up && prev_up == 0) {
      lcd.clear();
      indicator--;
      select--;
      prev_up = 1;
      Serial.println("UP");
    } else if (down && prev_down == 0) {
      lcd.clear();
      indicator++;
      select++;
      prev_down = 1;
      Serial.println("DOWN");
    }
    if (!up && prev_up == 1) {
      prev_up = 0;
    }
    if (!down && prev_down == 1) {
      prev_down = 0;
    }

    if (indicator == -1) {
      indicator = 0;
      disp--;
    }
    if (indicator == n_files + 1){
      indicator = n_files;
    }
    if (indicator == 4) {
      indicator = 3;
      disp++;
    }
    if (select == -1) {
      select = 0;
    }
    if (select == n_files + 1) {
      select = n_files;
    }

    if (disp == -1) {
      disp = 0;
    }
    if (disp == n_files - 2) {
      disp = n_files - 3;
    }

    writeLCD(lcd, "-", 0, indicator);

    for (int idx = 0; idx < 4; idx ++){
      if (disp + idx > n_files){
        break;
      }
      writeLCD(lcd, files[disp + idx], 2, idx);
    }


    if (enter) {
      lcd.clear();
      writeLCD(lcd, files[select], 0, 0);

      char* filename = (char*)malloc((strlen(files[select]) + 1) * sizeof(char));
      strcpy(filename, "/");
      strcat(filename, files[select]);
      return filename;
    }
  }
}

fs::FS init_SD(LiquidCrystal_I2C lcd) {
  if (!SD.begin(5)) {
    Serial.println("Card Mount Failed");
    writeLCD(lcd, "Card Mount Failed", 0, 0);
    return SD;
  }
  uint8_t cardType = SD.cardType();

  if (cardType == CARD_NONE) {
    writeLCD(lcd, "No SD card attached", 0, 0);
    return SD;
  }

  return SD;
}

void init_buttons(){
  pinMode(BUTTON_UP, INPUT_PULLUP);
  pinMode(BUTTON_DOWN, INPUT_PULLUP);
  pinMode(BUTTON_ENTER, INPUT_PULLUP);
}

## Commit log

2022-10-12 Add sample flybox Arduino code
2022-11-16 Add Arduino code and profile.json
2022-11-30 Uploading LED test code + Temp sensor
2022-12-01 Update LED One Bright.ino
2023-02-08 2/8 PCB schematics
    [FlyBoxBoard.kicad_pcb, FlyBoxBoard.kicad_sch, IR FANS LED board.kicad_pcb, IR FANS LED board.kicad_sch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]
2023-02-09 schematic now has no errors
    [FlyBoxBoard.kicad_sch, IR FANS LED board.kicad_sch, RGW LED board.kicad_sch]
2023-02-09 Labeling on components
    [FlyBoxBoard.kicad_sch, IR FANS LED board.kicad_sch, RGW LED board.kicad_sch]
2023-02-10 Layout progress
    [FlyBoxBoard.kicad_pcb]
2023-02-10 PCB progress
    [FlyBoxBoard.kicad_pcb, FlyBoxBoard.kicad_sch]
2023-02-10 Main PCB complete
    [FlyBoxBoard.kicad_pcb]
2023-02-13 Finished IR and RGW board
    [FlyBoxBoard.kicad_pcb, IR FANS LED board.kicad_pcb, RGW LED board.kicad_pcb]
2023-02-15 Zachary FlyBoxBoard review and edits
    [FlyBoxBoard.kicad_pcb]
2023-02-15 Ordering Fixes
    [FlyBoxBoard.kicad_pcb, RGW LED board-B_Cu.gbl, RGW LED board-B_Mask.gbs, RGW LED board-B_Silkscreen.gbo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]
2023-02-15 Zachary IR and RGW LED boards revisions
    [IR FANS LED board.kicad_pcb, RGW LED board.kicad_pcb]
2023-02-22 Gerber Files
    [FlyBoxBoard-B_Cu.gbr, FlyBoxBoard-B_Mask.gbr, FlyBoxBoard-B_Paste.gbr, FlyBoxBoard-B_Silkscreen.gbr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]
2023-02-22 Logos and labels
    [FlyBoxBoard-B_Cu.gbr, FlyBoxBoard-B_Mask.gbr, FlyBoxBoard-B_Paste.gbr, FlyBoxBoard-B_Silkscreen.gbr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]
2023-02-22 Removing old drill files
    [FlyBoxBoard-NPTH.drl, FlyBoxBoard-PTH.drl]
2023-03-01 Updated mounting holes and rounded corneres
    [FlyBoxBoard.kicad_pcb]
2023-03-01 3/1 updates
    [FlyBoxBoard.kicad_pcb, FlyBoxBoard.kicad_sch]
2023-03-01 3/1 Changes pt 2
    [FlyBoxBoard.kicad_pcb]
2023-03-08 modify how pin status is handled and also fix percent indicator
2023-03-08 3/8 Work
    Missing button footprint
    [FlyBoxBoard.kicad_pcb, FlyBoxBoard.kicad_sch]
2023-03-09 V2 IR and RGW boards done
    Main board missing button footprint
    [FlyBoxBoard.kicad_pcb, FlyBoxBoard.kicad_sch, IR FANS LED board.kicad_pcb, IR FANS LED board.kicad_sch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]
2023-03-09 Finished V2 PCBs with rounded edges
    [FlyBoxBoard.kicad_pcb, FlyBoxBoard.kicad_sch, IR FANS LED board.kicad_pcb, RGW LED board.kicad_pcb]
2023-03-09 Zachary first pass on V2 of FlyBoxBoard
    Not done yet, still need to look at/think about more.
    [FlyBoxBoard.kicad_pcb]
2023-03-09 Shrunk vias, fixed ohms and XV1 labels
    [FlyBoxBoard.kicad_pcb, FlyBoxBoard.kicad_sch, IR FANS LED board.kicad_pcb, RGW LED board.kicad_pcb]
2023-03-11 Zachary second pass on FlyBoxBoard
    Pretty much ready to go after OJ checks again and reviews my notes in Teams.
    I still have not checked the other two boards.
    [FlyBoxBoard.kicad_pcb]
2023-03-12 Zachary review of IR and RGW and Fans boards
    @oliviajobradley All done reviewing all three boards. I played with the silkscreen a bit, not sure if it's better or worse. OJ, feel free to change it back if you'd prefer.
    Let's order!
    [IR FANS LED board.kicad_pcb, RGW LED board.kicad_pcb]
2023-03-12 A few more PCB edits
    - Eliminated and/or shortened traces on rear side (no more long traces on the rear side)
    - Connected four screw vias on IR board to GND
    - Ran DRC on all boards and addressed issues where necessary
    Imo, we should be ready to order on @oliviajobradley's approval.
    [FlyBoxBoard.kicad_pcb, IR FANS LED board.kicad_pcb]
2023-03-22 Version 3 Assembly Edits
    [FlyBoxBoard-B_Cu.gbl, FlyBoxBoard-B_Mask.gbs, FlyBoxBoard-B_Paste.gbp, FlyBoxBoard-B_Silkscreen.gbo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]
2023-03-22 Fixed capitalization
    [FlyBoxBoard.kicad_pcb, IR FANS LED board.kicad_pcb, RGW LED board.kicad_pcb]
2023-03-22 Zachary final review of PCBs
    [FlyBoxBoard.kicad_pcb, IR FANS LED board.kicad_pcb]
2023-03-22 Adding board BOMs
    [FlyBoxBoard.csv, FlyBoxBoard.xlsx, IR FANS LED board.csv, IR FANS LED board.xlsx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]
2023-03-22 show current time in status screen
2023-03-28 V3 Gerbers and STEP Files
    [FlyBoxBoard-B_Cu.gbl, FlyBoxBoard-B_Mask.gbs, FlyBoxBoard-B_Paste.gbp, FlyBoxBoard-B_Silkscreen.gbo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]
2023-03-29 Centroid file
    [FlyBoxBoard.kicad_pcb]
2023-05-03 Added 3D print files
    [SD_card_and_rotary_encoder_mount.stl, camera_mount.stl, fan_baffle.stl, spacer.stl]
2023-05-03 Lasercut Files
2023-05-03 PCB Zip files
    [FlyBoxBoard-B_Cu.gbl, FlyBoxBoard-B_Mask.gbs, FlyBoxBoard-B_Paste.gbp, FlyBoxBoard-B_Silkscreen.gbo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]
2023-05-03 Uploading V2 of BOM and Instructions
    [Bill of Materials V2.xlsx]
2023-05-07 Version 3
    [Bill of Materials V2.xlsx, Bill of Materials.xlsx]
